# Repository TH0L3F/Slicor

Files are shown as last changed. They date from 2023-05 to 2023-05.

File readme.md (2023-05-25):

#  Slicor

Trancheuse de sable pour conçue pour le laboratoire de Sciences Naturelles de l'université de Lille

## Objectif

Trancher des blocs de sable de manière précise et sécuritaire pour faire un mapping 3D de ceux-ci afin de les étudier.

--------------------

## Construction

La trancheuse est constitué d'une structure rigide permettant d'interconnecter toute les parties mécanique utiles en un unique objet d'étude. Cette structure possède une plateau en métal sur lequel le bloc de sable doit se déplacer. Pour limiter les frottements il a était décidé de mettre une plaque en verre qui est lubrifier avant chaques utilisations. Pour absorber les chocs et limiter l'influence des variations de niveaux du plan en métal sur la plaque de verre (qui pourrait la fragiliser voir même la casser) une plaque en caoutchouc se trouve entre les deux plaques.

Une plaque mobile quand à elle permet de pousser le bloc de sable afin de le faire glisser sur la plaque en verre préalablement cité. Celui-ci est mis en mouvement par un vérin électrique. Un encodeur linéaire permet quand à lui de connaitre la position de la plaque à tous moment. Cette régle permet de mesurer des pats de déplacements dans un sens ou l'autre mais ne donne pas de référentiel c'est pourquoi un premier contacteur mécanique se trouve à l'extrémité zéro de la machine. Un second permet de savoir quand la plaque arrive en fin de course. Le vérin est contrôlé par un driver de moteur à courant continu lui même contrôler par une carte électronique (kicad de la carte dans le dossier électronique) permettant de récupérer les informations de tous les composants cités précédèment.

Un pupitre permet de faire l'interface homme-machine avec 3 voyants, respectivement : STOP (rouge), EN MOUVEMENT (JAUNE) et PRET (VERT) ainsi que deux boutons AVANT et ARRIERE. Un pavet numérique permet de sélectionner des valeurs avec un touche pour valider et 4 touches (A B C et D) permettant d'utiliser des valeurs preselectionnés. Un écran permet enfin d'afficher toute les informations nécessaires. Tous ces composants sont interconnectés via une autre carte électronique (kicad de la carte dans le dossier électronique). Le pupitre contient aussi l'alimentation, un bouton marche arret, et un bouton d'arrêt d'urgence.

Les deux cartes sont interconnectés via une liaison série (RX TX) UART afin permettre dans un sens d'envoyer les ordres et de recevoir dans l'autre sens un feedback de ce qui se passe.

--------------------

## Fonctionnement  

Dans un premier temps l'utilisateur fait le homming de la machine (la mise à zéro) afin que celle-ci se déplace pour se mettre en contact avec le premier contacteur.

Puis l'utilisateur entre une valeur et la valide sur le pavé.

Enfin il peut appuyer sur le bouton AVANT ou ARRIERE afin de déplacer le vérin et donc le bloc de sable de la distance souhaitée.

La valeur de déplacement peut être changer en dehors des moments de mouvements. Il faut alors à nouveau valider.

--------------------

## Préparation

Il faut mettre en position zéro la machine après chaques utilisations pour facilité la préparation de la fois suivante.

Premièrement il faut huiler la plaque de verre pour faciliter le déplacement.

Puis disposer le bloc de sable en buter sur la plaque mobile et le plan perpendiculaire à la plaque mobile.

Puis faire les étapes de fonctionnement précisé ci-dessus.

--------------------

#AUTRE

## Programmation

Pour programmer il faut utiliser un programmateur spécifique et le connecteur correspondant sur la carte. Le programmateur est le même que le programmateur du projet Slicor. Une petite fléche permet sur la carte et le connecteur du programmateur permet de détromper le sens de connexion. Ensuite via l'IDE arduino il est possible de mettre le bootloader ("carte : arduino uno", "programmateur : TINYasISP" puis "burn bootloader") il est nécessaire de mettre le bootloader si la puce n'en a pas déjà. Ensuite avec l'option "programmer via un programmateur" il est possible de téléverser le programmer dans le microcontrôleur.

#### ATTENTION !!!
Avec le programmeteur mis à dispositon une erreur survient dans certaine condition. Si un timeout est émis par le programmateur une solution est d'enlever ou d'ajouter des delay(1) dans la partie setup du programme. (Si une meilleure solution existe je suis preneur).

## TODO

### Mécanique
-Monter les pièces usinés (Douille à bille avec pièce en acier et circlips
-Faire souder la structure porteuse de plateau
-Fixer le plan de pousser sur la structure souder
-Fixer les douilles sur la structure souder
-Fixer les pièces fesant le lien entre la structure souder et le vérin
-Installer les équerres de support des tiges
-Vérifier le positionnement
-Modéliser et fabriquer un support pour l'autre extremité du vérin
-La fixer directement sur la plaque en acier
-Faire le lien entre l'encodeur linéaire et la structure souder (mesure direct de la position)
-Fixer une lame sur le mobile de découpe de façon sécuritaire et précise

#### Attention !!!
-Ne pas retirer les douilles des tiges (ça les abimes)
-Vérifier le parallèlisme avant d'appliquer le moindre effort (sinon la structure risque d'être détruite)
-Traiter le cadre pour limiter les risques de rouilles (milieu humide et sable)

### Programmation
-Vérifier la communication entre les deux cartes
-Programmer le PID (vérin - encodeur linéaire) pour le mouvement de la plaque
-Vérifier le sens des contacteurs

#### Attention !!!
-Faire les premiers tests à vide et toujours à porter de bouton d'arrêt d'urgence
-Programmer avec le même programmateur que le subductor
-Parfois la programmation ne fonctionne pas et nécessite l'ajout ou le retrait de delay(1) à des endroits dans le programme (Dont know why ...)
-Vérifier le sens de branchement des deux contacteurs fin de course

### Manuel
-Modifier le manuel si nécessaire après avoir expérimenté ce qui est actuellement proposé

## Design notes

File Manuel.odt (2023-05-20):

Manuel d'utilisation de la

machine Slicor

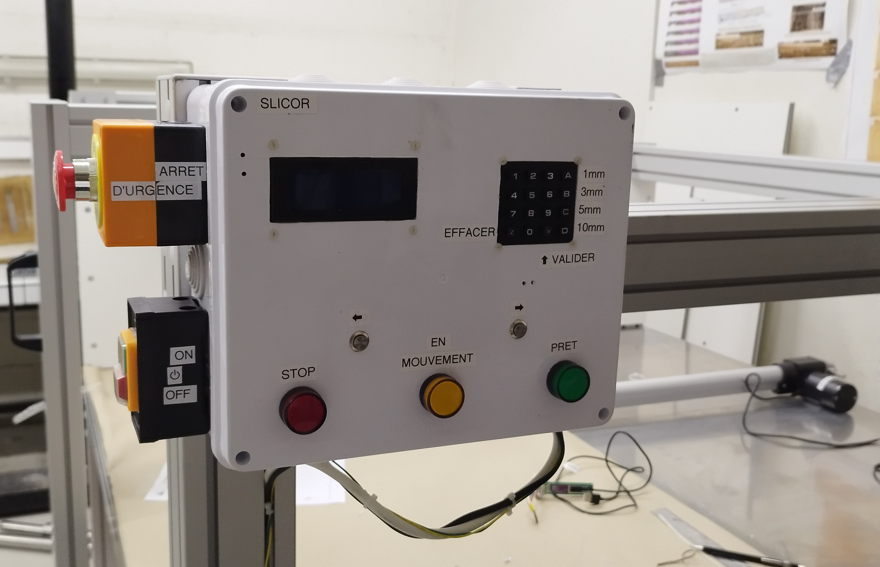
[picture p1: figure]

INTRODUCTION

La machine slicor permet de découper des blocs de sable de différentes tailles en tranche de façon précise. Cette machine est équipée d'un vérin électrique qui pousse le bloc de sable poser sur une plaque de verre qui sera ensuite découpé par l’utilisateur à l’aide d’un mobile sur lequel une lame est attachée.

SÉCURITÉ

La sécurité est primordiale lors de l'utilisation de la machine de découpe de blocs de sable. Voici les mesures à prendre :

1. Ne pas toucher l’intérieur de la machine pendant son fonctionnement.
2. Ne pas dépasser la plage de mouvement.
3. Utiliser le bouton d’arrêt d’urgence en cas de danger ou de problème.
4. Ne pas laisser la machine sans surveillance pendant son utilisation.
5. Ne pas dépasser la charge maximale de la machine (500Kg).

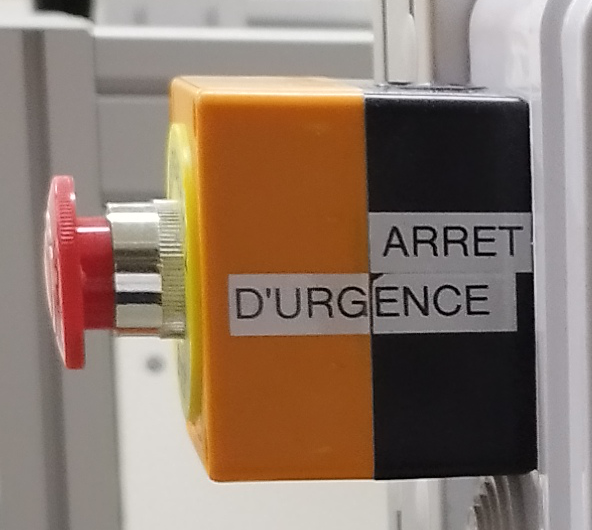
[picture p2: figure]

ÉTAPES DE PREPARATION

Étape 1 : Retirer tout ce qui se trouve autour de la machine et qui pourrait gêner son fonctionnement.

Étape 2 : Vérifier qu'il n'y a rien derrière la plaque (du côté de l'accroche du vérin).

Étape 3 : Nettoyer la surface devant et derrière le plan de poussée de la machine.

Étape 4 : Démarrer la machine.

Étape 5 : Effectuer la procédure de retour à la position initiale de la machine (homing).

Étape 6 : Appliquer une graisse minérale adaptée sur la surface en verre.

Étape 7 : Charger le bloc de sable sur le plan en verre.

Étape 8 : Positionner le bloc de sable contre le plan de poussée.

La machine et le bloc de sable sont maintenant prêts pour le découpage.

ÉTAPES DE TRANCHAGE

Étape 1 : Sélectionner à l'aide du clavier la valeur du déplacement souhaité.

Étape 2 : Vérifier sur l'écran que la valeur souhaitée est bien inscrite.

Étape 3 : Confirmer la valeur en utilisant la touche appropriée du clavier.

Étape 4 : Appuyer sur le bouton avant ou arrière pour déplacer le vérin selon la valeur indiquée

Étape 5 : Effectuer un mouvement aller avec le dispositif de tranchage pour réaliser une tranche.

Étape 6 : Effectuer un mouvement de retour pour replacer le dispositif de tranchage au début de la course.

Pour effectuer plusieurs tranches successives : répéter les étapes 4, 5 et 6 autant de fois que nécessaire tout en veillant à respecter les règles de sécurité.

Pour modifier l'épaisseur des tranches, refaire les étapes 1, 2 et 3.

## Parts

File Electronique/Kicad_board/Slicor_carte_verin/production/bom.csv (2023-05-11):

Designator | Footprint | Quantity | Value | LCSC Part #
C1 | C_Elec_10x10.2 | 1 | 680uF
C2 | C_Elec_10x10.2 | 1 | 220uF
C3, C4 | C_01005_0402Metric | 2 | 22p
D5 | D_SOD-128 | 1 | 1N5824
L1 | L_7.3x7.3_H4.5 | 1 | 33uH
R13 | R_1206_3216Metric | 1 | 100k
U1 | TO-263-5_TabPin3 | 1 | LM2596S-5
Y1 | Crystal_SMD_3225-4Pin_3.2x2.5mm | 1 | 16MHz
uC1 | TQFP-32_7x7mm_P0.8mm | 1 | ATmega328-A

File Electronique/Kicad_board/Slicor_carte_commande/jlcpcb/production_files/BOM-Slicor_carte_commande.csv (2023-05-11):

Comment | Designator | Footprint | LCSC
16MHz | Y1 | Crystal_SMD_3225-4Pin_3.2x2.5mm | C13738
ATmega328-A | uC1 | TQFP-32_7x7mm_P0.8mm | C14877
22p | C3,C4 | C_0402_1005Metric | C1555
100k | R13 | R_1206_3216Metric | C17900
10k | R1,R2 | R_1206_3216Metric | C17902
2k | R3,R4,R5 | R_1206_3216Metric | C17944
LM2596S-5 | U1 | TO-263-5_TabPin3 | C194349
S8050 | Q1,Q2,Q3 | SOT-23-3 | C2146
Shottky 24 5V | D5 | D_SOD-128 | C2766156
680uF | C1 | C_Elec_10x10.2 | C335987
220uF | C2 | C_Elec_10x10.2 | C393833
1k | R6 | R_1206_3216Metric | C4410
33uH | L1 | L_7.3x7.3_H4.5 | C514809
LED | D1 | LED_0805_2012Metric | C84256
TestPoint | TP4 | TestPoint_Pad_1.5x1.5mm
TestPoint | TP3 | TestPoint_Pad_1.5x1.5mm
TestPoint | TP2 | TestPoint_Pad_1.5x1.5mm
TestPoint | TP1 | TestPoint_Pad_1.5x1.5mm
Connecteur_Alim | J1 | TerminalBlock_bornier-2_P5.08mm
Connecteur_bouton_1 | J5 | JST_XH_B2B-XH-A_1x02_P2.50mm_Vertical
Connecteur_led_3 | J9 | JST_XH_B2B-XH-A_1x02_P2.50mm_Vertical
Connecteur_ecran | J2 | JST_XH_B4B-XH-A_1x04_P2.50mm_Vertical
Connecteur_Prog | J4 | PinHeader_1x08_P2.54mm_Vertical
Connecteur_led_2 | J8 | JST_XH_B2B-XH-A_1x02_P2.50mm_Vertical
Connecteur_clavier_1 | J3 | JST_XH_S4B-XH-A_1x04_P2.50mm_Horizontal
MountingHole_Pad | H1 | MountingHole_4.3mm_M4_DIN965_Pad
Connecteur_communication | J10 | JST_XH_B2B-XH-A_1x02_P2.50mm_Vertical
Connecteur_led_1 | J7 | JST_XH_B2B-XH-A_1x02_P2.50mm_Vertical
MountingHole_Pad | H4 | MountingHole_4.3mm_M4_DIN965_Pad
Connecteur_bouton_2 | J6 | JST_XH_B2B-XH-A_1x02_P2.50mm_Vertical
MountingHole_Pad | H3 | MountingHole_4.3mm_M4_DIN965_Pad
MountingHole_Pad | H2 | MountingHole_4.3mm_M4_DIN965_Pad
Connecteur_clavier_2 | J11 | JST_XH_S4B-XH-A_1x04_P2.50mm_Horizontal

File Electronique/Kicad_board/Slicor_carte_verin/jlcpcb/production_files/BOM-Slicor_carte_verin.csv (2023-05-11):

Comment | Designator | Footprint | LCSC
16MHz | Y1 | Crystal_SMD_3225-4Pin_3.2x2.5mm | C13738
ATmega328-A | uC1 | TQFP-32_7x7mm_P0.8mm | C14877
22p | C3,C4 | C_01005_0402Metric | C1555
100k | R13 | R_1206_3216Metric | C17900
10k | R1,R2 | R_1206_3216Metric | C17902
LM2596S-5 | U1 | TO-263-5_TabPin3 | C194349
1N5824 | D5 | D_SOD-128 | C2766156
680uF | C1 | C_Elec_10x10.2 | C335987
220uF | C2 | C_Elec_10x10.2 | C393833
33uH | L1 | L_7.3x7.3_H4.5 | C514809
Conn_encodeur_linear | J5 | JST_XH_B4B-XH-A_1x04_P2.50mm_Vertical
Connecteur_Comm | J3 | JST_XH_B2B-XH-A_1x02_P2.50mm_Vertical
Conn_mot_2 | J7 | JST_XH_B4B-XH-A_1x04_P2.50mm_Vertical
Conn_mot_1 | J6 | JST_XH_B4B-XH-A_1x04_P2.50mm_Vertical
Connecteur_Moteur | J2 | TerminalBlock_bornier-2_P5.08mm
MountingHole_Pad | H2 | MountingHole_4mm_Pad_Via
Connecteur_Alim | J1 | TerminalBlock_bornier-2_P5.08mm
MountingHole_Pad | H4 | MountingHole_4mm_Pad_Via
MountingHole_Pad | H1 | MountingHole_4mm_Pad_Via
Connecteur_Prog | J4 | PinHeader_1x08_P2.54mm_Vertical
MountingHole_Pad | H3 | MountingHole_4mm_Pad_Via
Conn_contacteur_A | J9 | JST_XH_B2B-XH-A_1x02_P2.50mm_Vertical
Conn_contacteur_B | J8 | JST_XH_B2B-XH-A_1x02_P2.50mm_Vertical

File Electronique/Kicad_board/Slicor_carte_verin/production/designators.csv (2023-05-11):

C1:1
C2:1
C3:1
C4:1
D5:1
H1:1
H2:1
H3:1
H4:1
J1:1
J2:1
J3:1
J4:1
J5:1
J6:1
J7:1
L1:1
R13:1
U1:1
Y1:1
uC1:1

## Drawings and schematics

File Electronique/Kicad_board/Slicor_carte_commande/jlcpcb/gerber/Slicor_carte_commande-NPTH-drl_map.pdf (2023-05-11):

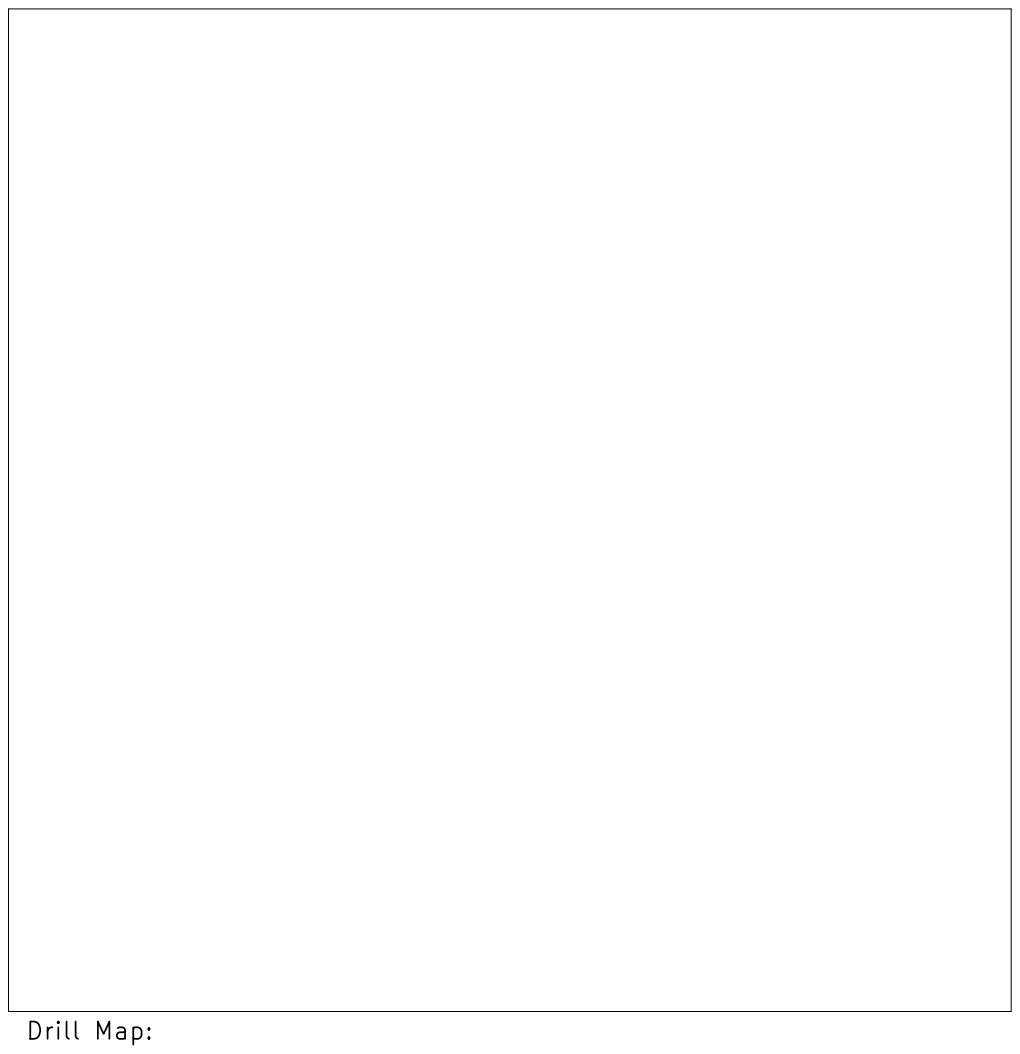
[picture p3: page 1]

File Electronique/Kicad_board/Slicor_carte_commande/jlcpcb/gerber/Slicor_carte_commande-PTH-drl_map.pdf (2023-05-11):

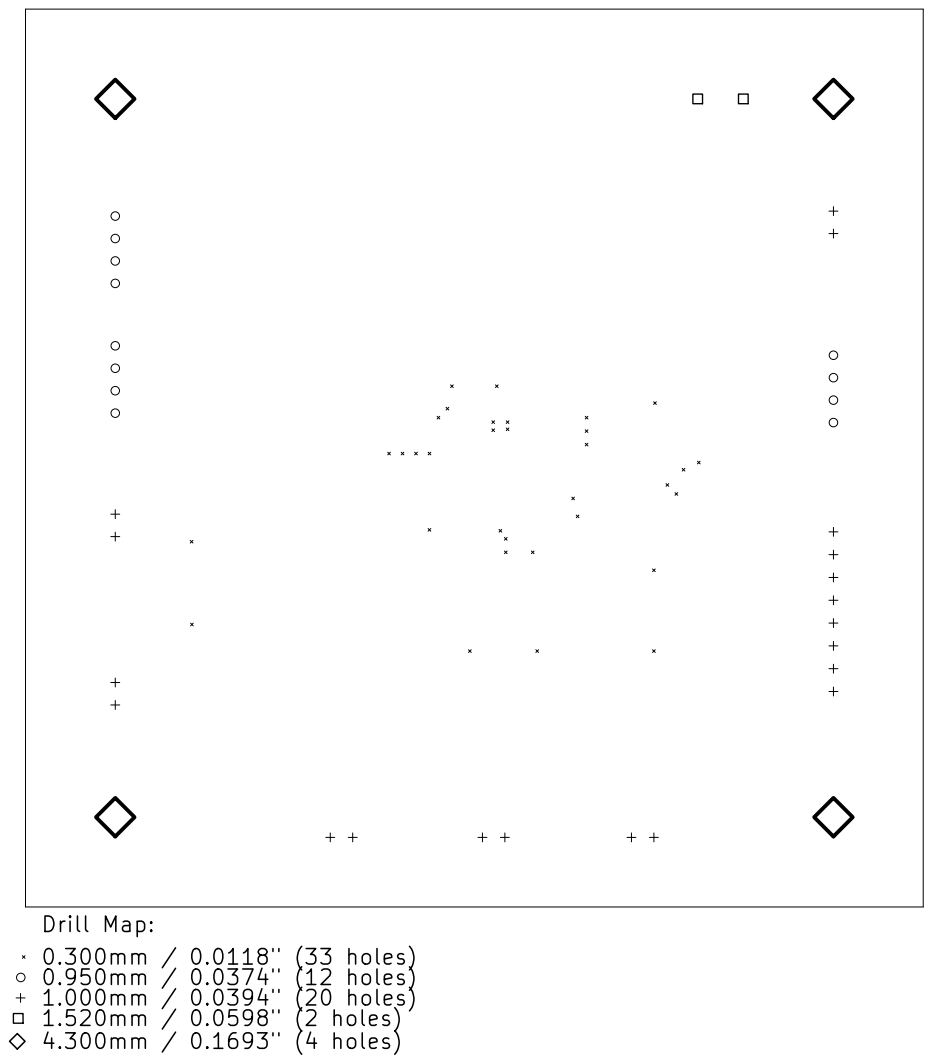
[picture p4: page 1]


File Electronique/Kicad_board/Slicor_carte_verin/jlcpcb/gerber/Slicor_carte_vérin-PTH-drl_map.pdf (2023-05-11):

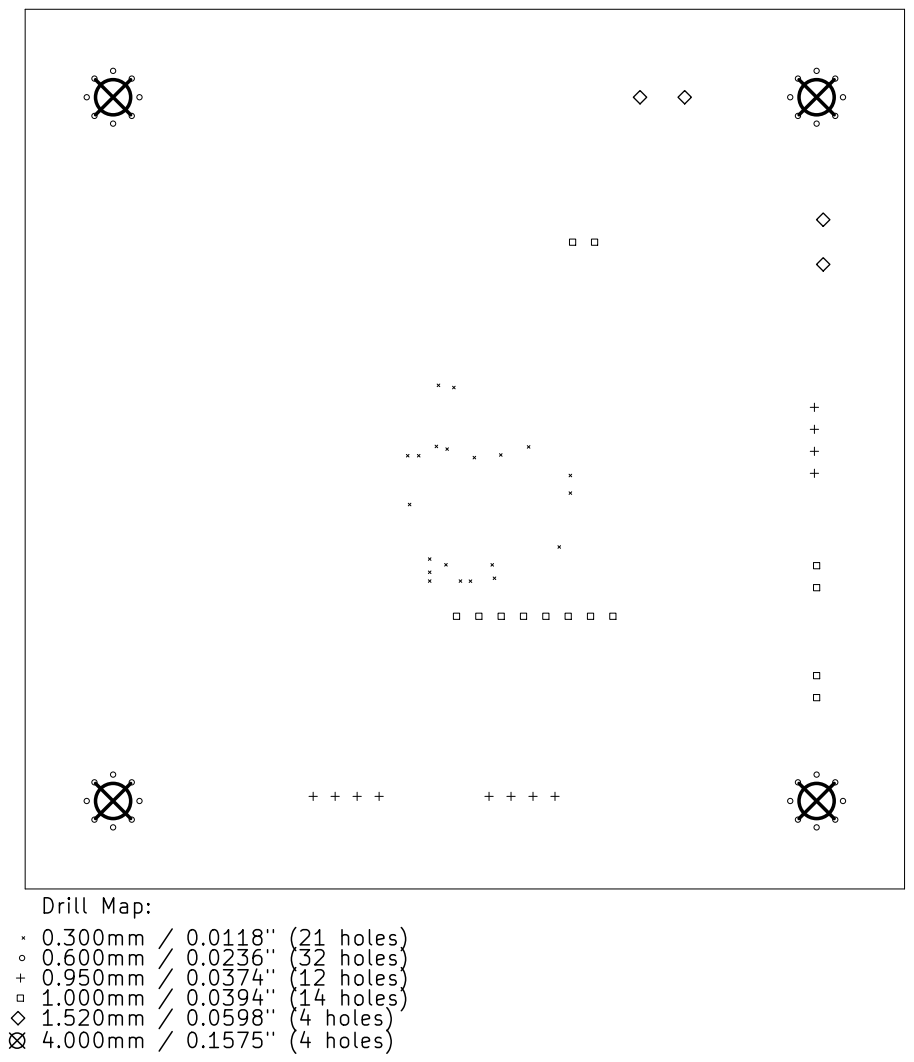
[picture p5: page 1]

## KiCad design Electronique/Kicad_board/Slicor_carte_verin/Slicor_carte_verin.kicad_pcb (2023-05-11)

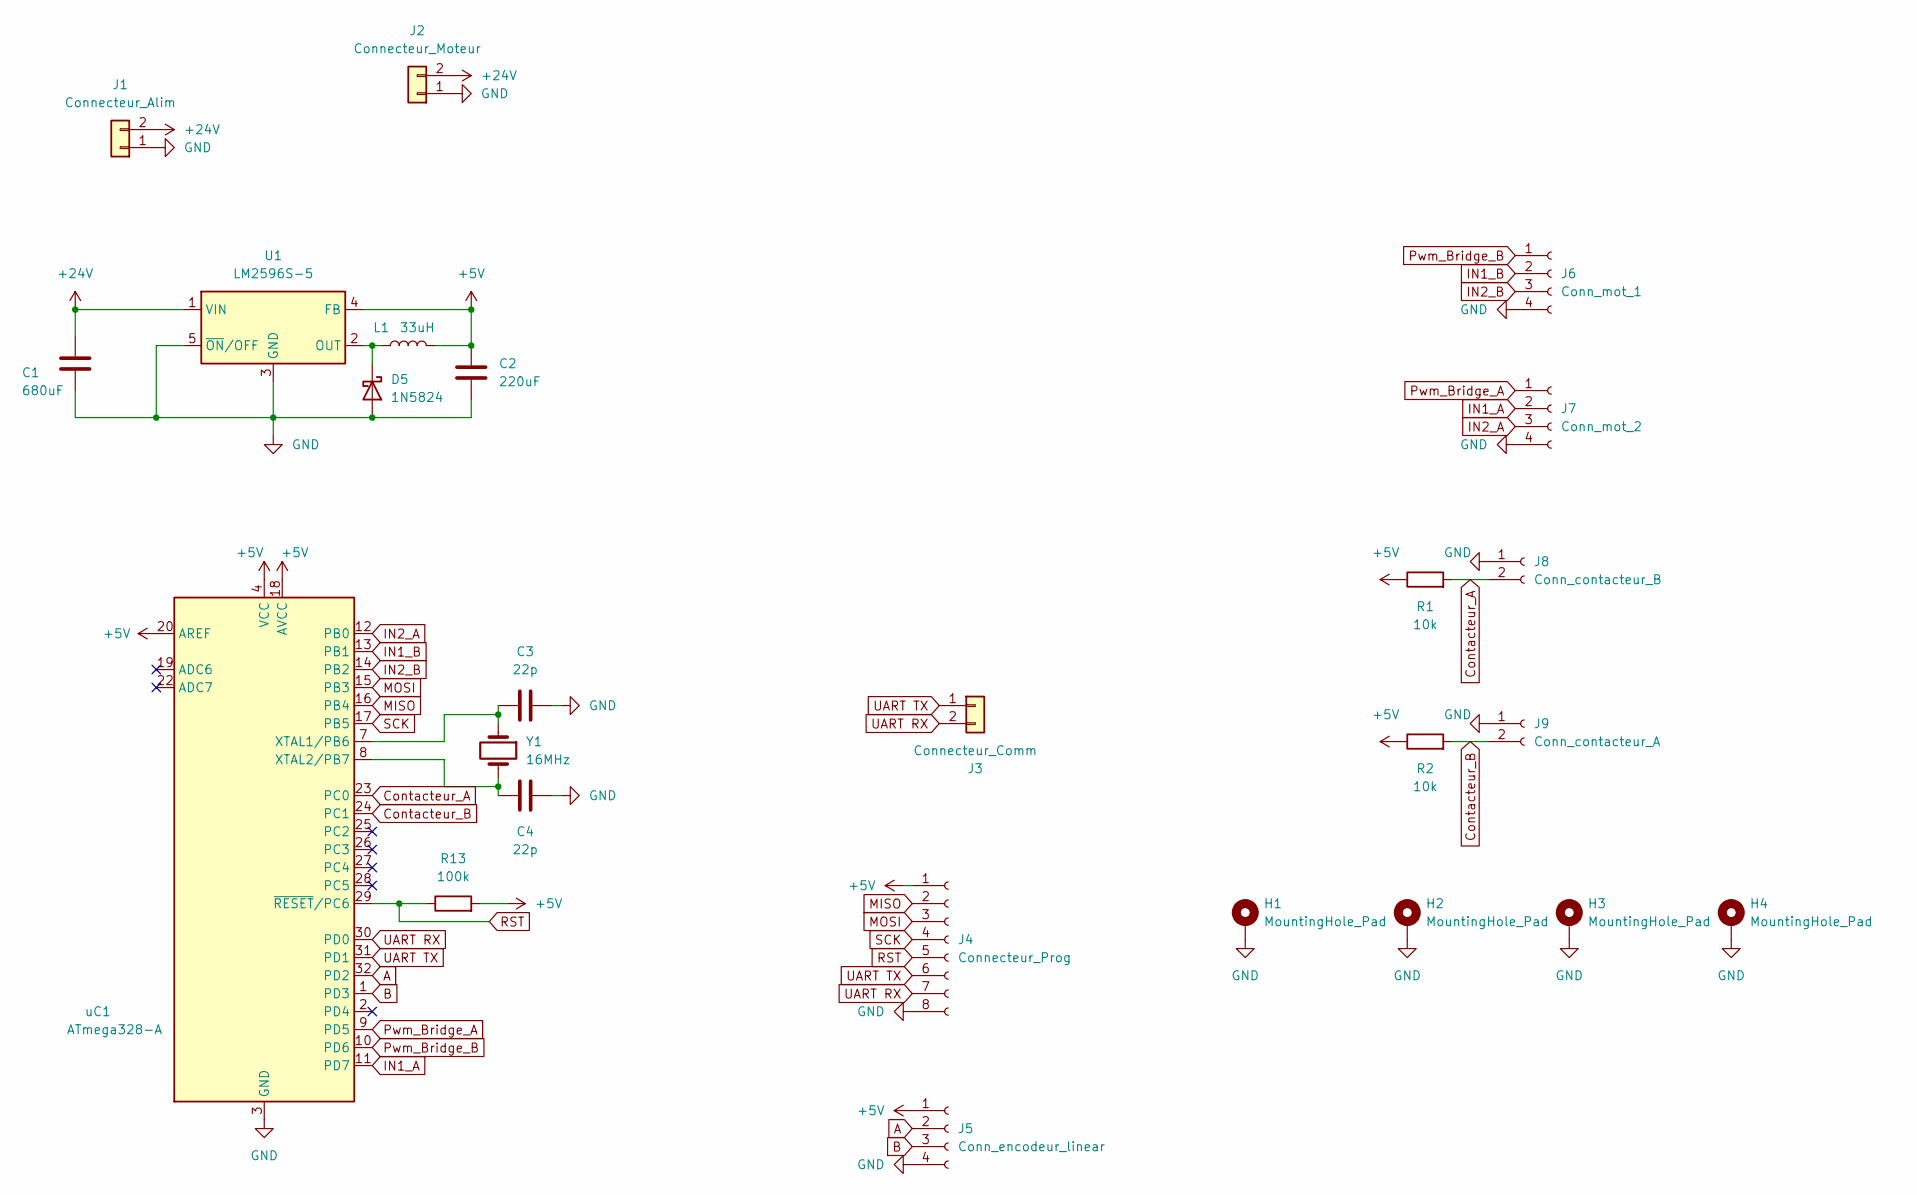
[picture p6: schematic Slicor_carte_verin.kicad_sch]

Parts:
C1: 680uF; C_Elec_10x10.2
C2: 220uF; C_Elec_10x10.2
C3, C4: 22p; C_01005_0402Metric
D5: 1N5824; D_SOD-128
H1, H2, H3, H4: MountingHole_Pad; MountingHole_4mm_Pad_Via
J1: Connecteur_Alim; TerminalBlock_bornier-2_P5.08mm
J2: Connecteur_Moteur; TerminalBlock_bornier-2_P5.08mm
J3: Connecteur_Comm; JST_XH_B2B-XH-A_1x02_P2.50mm_Vertical
J4: Connecteur_Prog; PinHeader_1x08_P2.54mm_Vertical
J5: Conn_encodeur_linear; JST_XH_B4B-XH-A_1x04_P2.50mm_Vertical
J6: Conn_mot_1; JST_XH_B4B-XH-A_1x04_P2.50mm_Vertical
J7: Conn_mot_2; JST_XH_B4B-XH-A_1x04_P2.50mm_Vertical
J8: Conn_contacteur_B; JST_XH_B2B-XH-A_1x02_P2.50mm_Vertical
J9: Conn_contacteur_A; JST_XH_B2B-XH-A_1x02_P2.50mm_Vertical
L1: 33uH; L_7.3x7.3_H4.5
R1, R2: 10k; R_1206_3216Metric
R13: 100k; R_1206_3216Metric
U1: LM2596S-5; TO-263-5_TabPin3
Y1: 16MHz; Crystal_SMD_3225-4Pin_3.2x2.5mm
uC1: ATmega328-A; TQFP-32_7x7mm_P0.8mm

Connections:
+5V: C2.1, J4.1, J5.1, L1.2, R1.1, R2.1, R13.2, U1.4 (FB), uC1.4 (VCC), uC1.6 (VCC), uC1.18 (AVCC), uC1.20 (AREF)
+24V: C1.1, J1.2, J2.2, U1.1 (VIN)
A: J5.2, uC1.32 (PD2)
B: J5.3, uC1.1 (PD3)
Contacteur_A: J8.2, R1.2, uC1.23 (PC0)
Contacteur_B: J9.2, R2.2, uC1.24 (PC1)
GND: C1.2, C2.2, C3.2, C4.2, D5.2 (A), H1.1, H2.1, H3.1, H4.1, J1.1, J2.1, J4.8, J5.4, J6.4, J7.4, J8.1, J9.1, U1.3 (GND), U1.5 (~ON/OFF), uC1.3 (GND), uC1.5 (GND), uC1.21 (GND)
IN1_A: J7.2, uC1.11 (PD7)
IN1_B: J6.2, uC1.13 (PB1)
IN2_A: J7.3, uC1.12 (PB0)
IN2_B: J6.3, uC1.14 (PB2)
MISO: J4.2, uC1.16 (PB4)
MOSI: J4.3, uC1.15 (PB3)
unnamed: C3.1, Y1.1, uC1.7 (XTAL1/PB6)
unnamed: C4.1, Y1.2, uC1.8 (XTAL2/PB7)
unnamed: D5.1 (K), L1.1, U1.2 (OUT)
Pwm_Bridge_A: J7.1, uC1.9 (PD5)
Pwm_Bridge_B: J6.1, uC1.10 (PD6)
RST: J4.5, R13.1, uC1.29 (~RESET/PC6)
SCK: J4.4, uC1.17 (PB5)
UART RX: J3.2, J4.7, uC1.30 (PD0)
UART TX: J3.1, J4.6, uC1.31 (PD1)

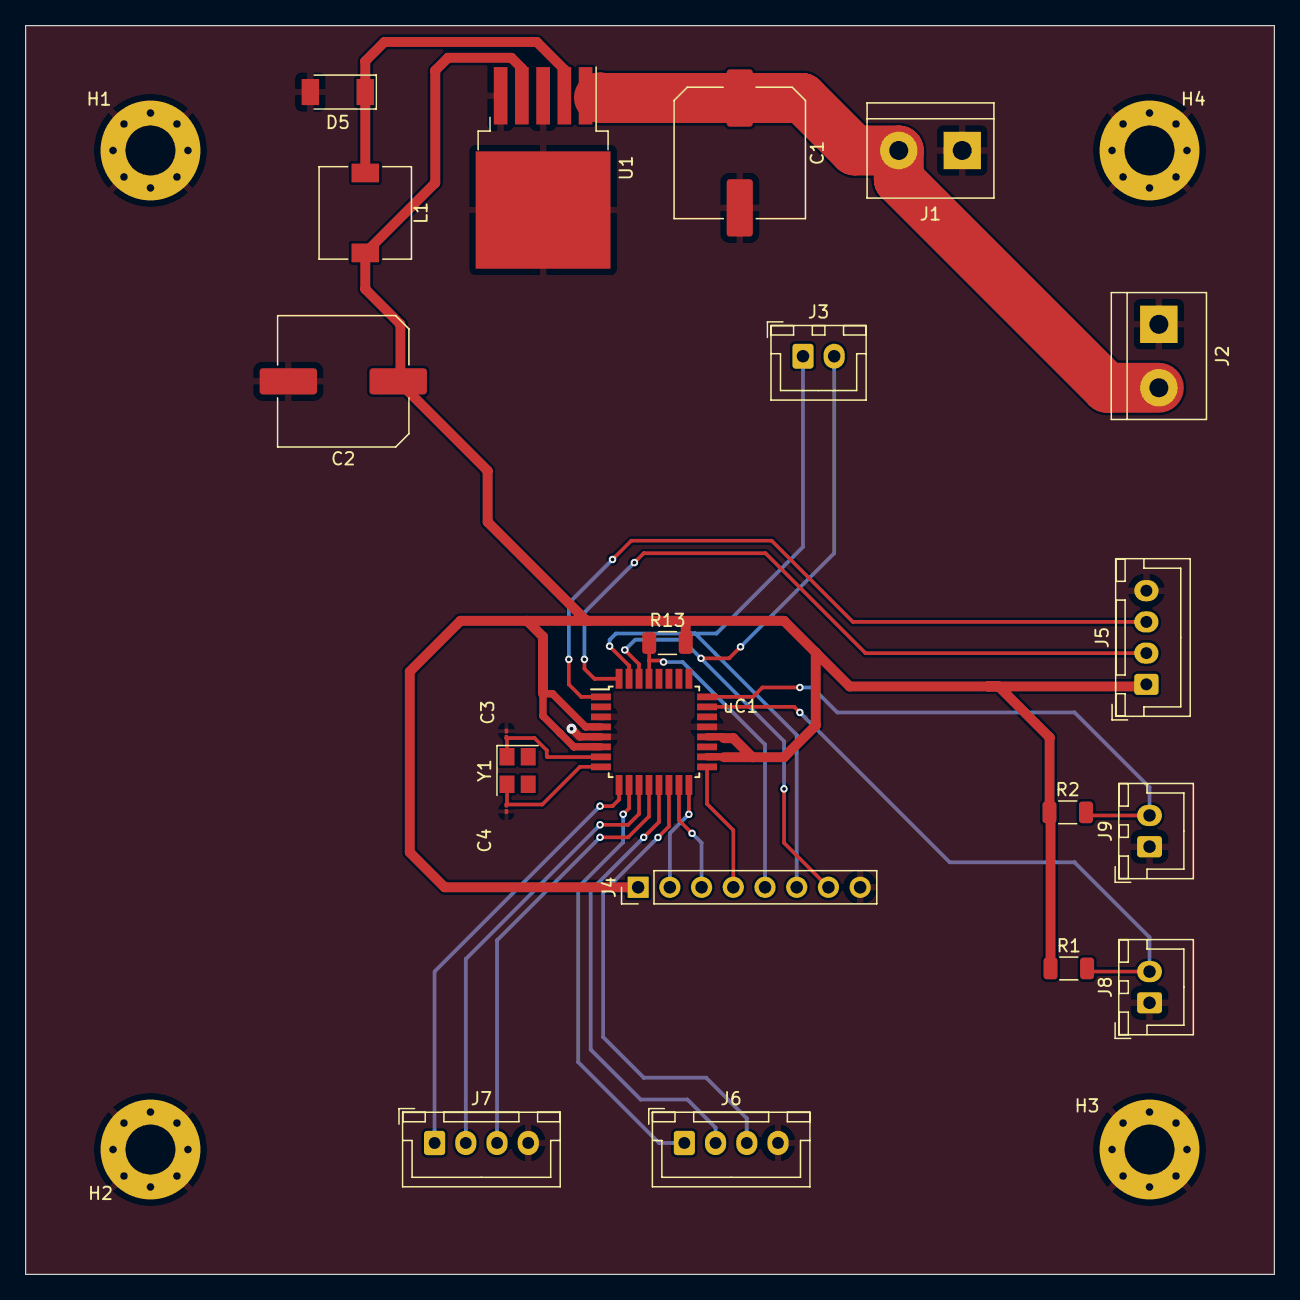
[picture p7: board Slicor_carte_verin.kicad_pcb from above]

Board: 4 copper layers, 100.0 x 100.0 mm, 25 parts (0 on the bottom side), 22 nets.

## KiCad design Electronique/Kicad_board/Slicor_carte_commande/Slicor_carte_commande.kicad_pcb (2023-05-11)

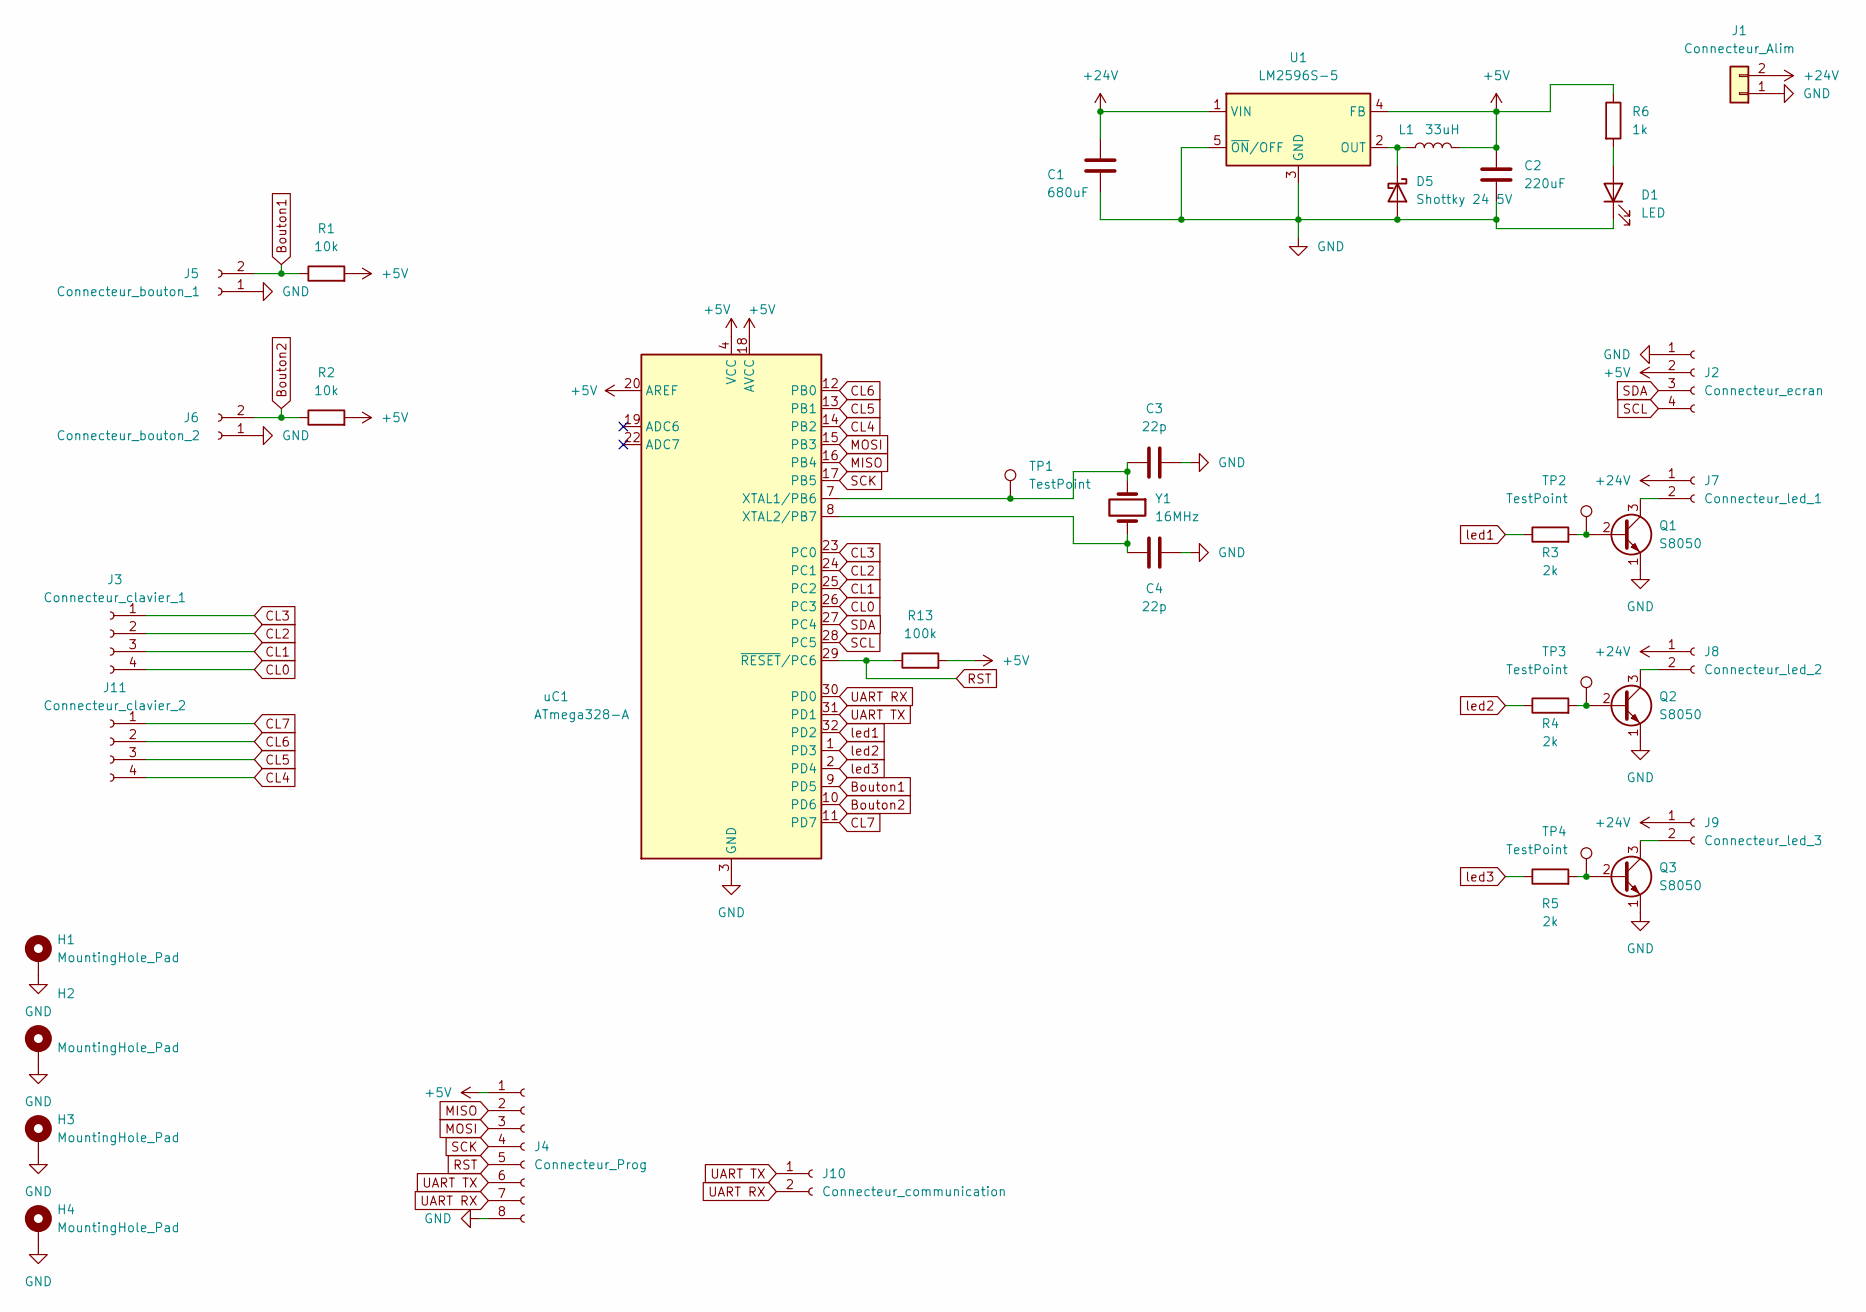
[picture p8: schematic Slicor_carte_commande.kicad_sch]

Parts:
C1: 680uF; C_Elec_10x10.2
C2: 220uF; C_Elec_10x10.2
C3, C4: 22p; C_0402_1005Metric
D1: LED; LED_0805_2012Metric
D5: Shottky 24 5V; D_SOD-128
H1, H2, H3, H4: MountingHole_Pad; MountingHole_4.3mm_M4_DIN965_Pad
J1: Connecteur_Alim; TerminalBlock_bornier-2_P5.08mm
J2: Connecteur_ecran; JST_XH_B4B-XH-A_1x04_P2.50mm_Vertical
J3: Connecteur_clavier_1; JST_XH_S4B-XH-A_1x04_P2.50mm_Horizontal
J4: Connecteur_Prog; PinHeader_1x08_P2.54mm_Vertical
J5: Connecteur_bouton_1; JST_XH_B2B-XH-A_1x02_P2.50mm_Vertical
J6: Connecteur_bouton_2; JST_XH_B2B-XH-A_1x02_P2.50mm_Vertical
J7: Connecteur_led_1; JST_XH_B2B-XH-A_1x02_P2.50mm_Vertical
J8: Connecteur_led_2; JST_XH_B2B-XH-A_1x02_P2.50mm_Vertical
J9: Connecteur_led_3; JST_XH_B2B-XH-A_1x02_P2.50mm_Vertical
J10: Connecteur_communication; JST_XH_B2B-XH-A_1x02_P2.50mm_Vertical
J11: Connecteur_clavier_2; JST_XH_S4B-XH-A_1x04_P2.50mm_Horizontal
L1: 33uH; L_7.3x7.3_H4.5
Q1, Q2, Q3: S8050; SOT-23-3
R1, R2: 10k; R_1206_3216Metric
R3, R4, R5: 2k; R_1206_3216Metric
R6: 1k; R_1206_3216Metric
R13: 100k; R_1206_3216Metric
TP1, TP2, TP3, TP4: TestPoint; TestPoint_Pad_1.5x1.5mm
U1: LM2596S-5; TO-263-5_TabPin3
Y1: 16MHz; Crystal_SMD_3225-4Pin_3.2x2.5mm
uC1: ATmega328-A; TQFP-32_7x7mm_P0.8mm

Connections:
+5V: C2.1, J2.2, J4.1, L1.2, R1.2, R2.2, R6.1, R13.2, U1.4 (FB), uC1.4 (VCC), uC1.6 (VCC), uC1.18 (AVCC), uC1.20 (AREF)
+24V: C1.1, J1.2, J7.1, J8.1, J9.1, U1.1 (VIN)
Bouton1: J5.2, R1.1, uC1.9 (PD5)
Bouton2: J6.2, R2.1, uC1.10 (PD6)
CL0: J3.4, uC1.26 (PC3)
CL1: J3.3, uC1.25 (PC2)
CL2: J3.2, uC1.24 (PC1)
CL3: J3.1, uC1.23 (PC0)
CL4: J11.4, uC1.14 (PB2)
CL5: J11.3, uC1.13 (PB1)
CL6: J11.2, uC1.12 (PB0)
CL7: J11.1, uC1.11 (PD7)
GND: C1.2, C2.2, C3.2, C4.2, D1.1 (K), D5.2 (A), H1.1, H2.1, H3.1, H4.1, J1.1, J2.1, J4.8, J5.1, J6.1, Q1.1 (E), Q2.1 (E), Q3.1 (E), U1.3 (GND), U1.5 (~ON/OFF), uC1.3 (GND), uC1.5 (GND), uC1.21 (GND); also elsewhere on the board
MISO: J4.2, uC1.16 (PB4)
MOSI: J4.3, uC1.15 (PB3)
unnamed: C3.1, TP1.1, Y1.1, uC1.7 (XTAL1/PB6)
unnamed: C4.1, Y1.2, uC1.8 (XTAL2/PB7)
unnamed: D1.2 (A), R6.2
unnamed: D5.1 (K), L1.1, U1.2 (OUT)
unnamed: J7.2, Q1.3 (C)
unnamed: J8.2, Q2.3 (C)
unnamed: J9.2, Q3.3 (C)
unnamed: Q1.2 (B), R3.2, TP2.1
unnamed: Q2.2 (B), R4.2, TP3.1
unnamed: Q3.2 (B), R5.2, TP4.1
RST: J4.5, R13.1, uC1.29 (~RESET/PC6)
SCK: J4.4, uC1.17 (PB5)
SCL: J2.4, uC1.28 (PC5)
SDA: J2.3, uC1.27 (PC4)
UART RX: J4.7, J10.2, uC1.30 (PD0)
UART TX: J4.6, J10.1, uC1.31 (PD1)
led1: R3.1, uC1.32 (PD2)
led2: R4.1, uC1.1 (PD3)
led3: R5.1, uC1.2 (PD4)

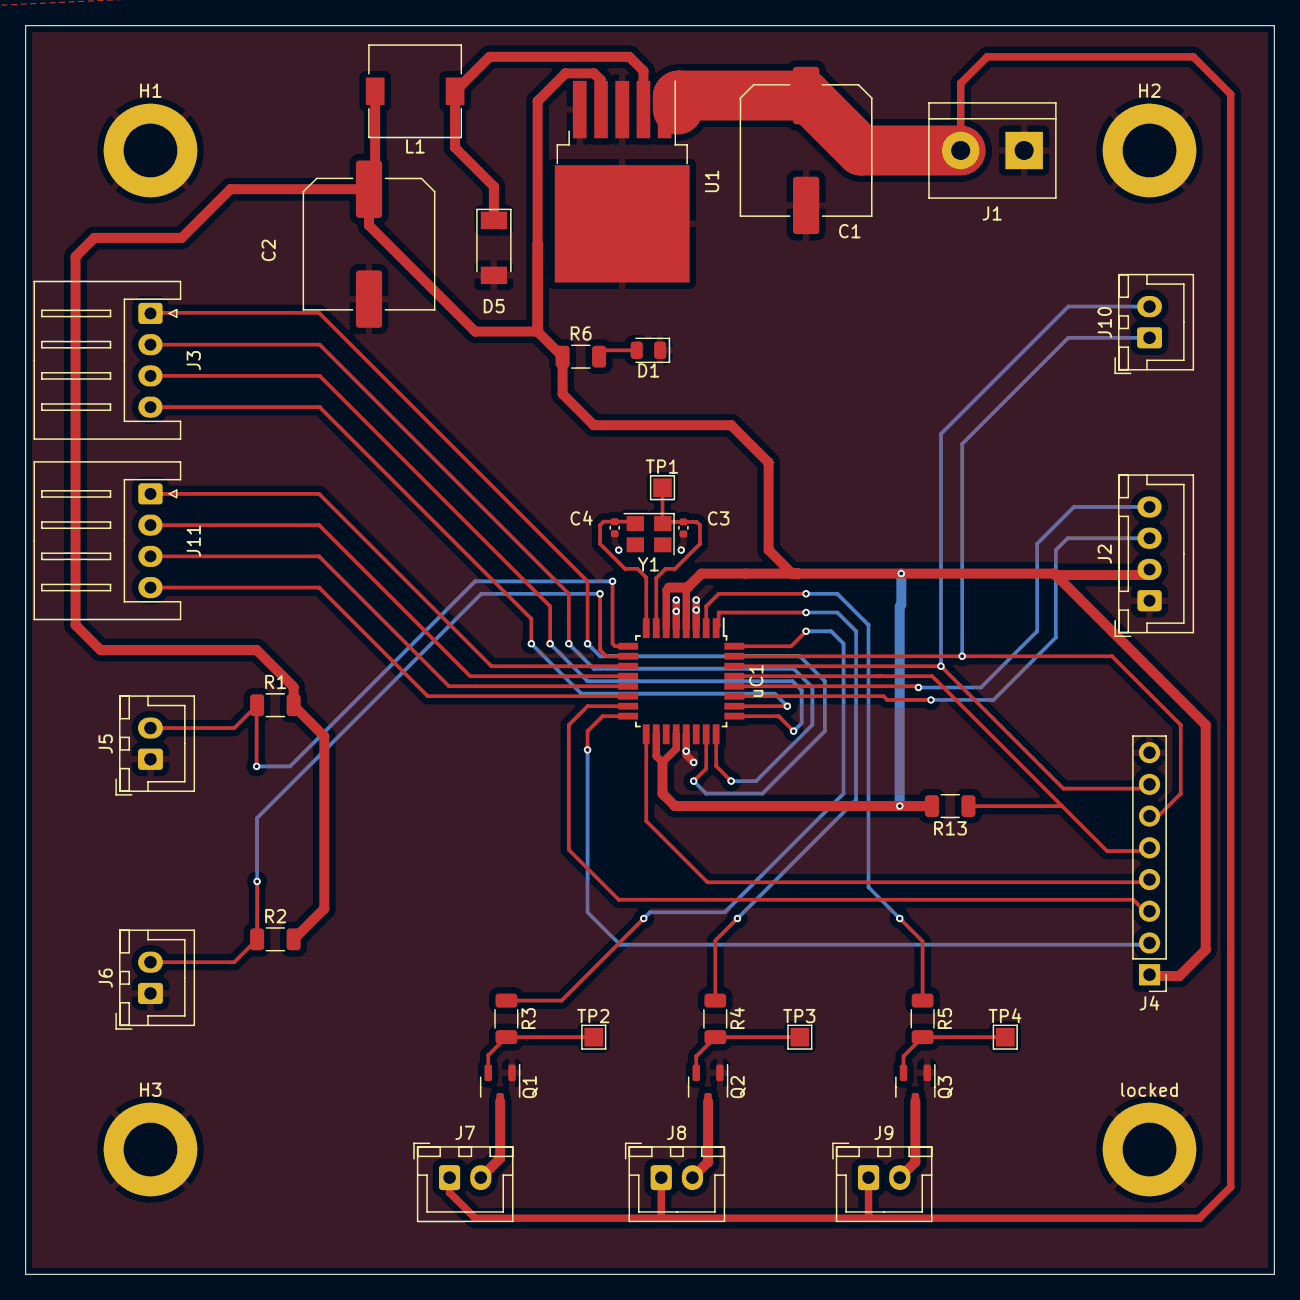
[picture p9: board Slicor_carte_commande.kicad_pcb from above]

Board: 4 copper layers, 100.0 x 100.0 mm, 39 parts (0 on the bottom side), 34 nets.

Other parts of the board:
locked: MountingHole_Pad; MountingHole_4.3mm_M4_DIN965_Pad

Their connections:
GND: locked.1; also elsewhere on the board

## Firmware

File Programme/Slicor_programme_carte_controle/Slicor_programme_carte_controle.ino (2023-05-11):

//Utilitaire pour l'écran LCD
#include <Wire.h> 
#include <LiquidCrystal_I2C.h>
#define len_lcd 20 //Nombre de caractère en longueur de l'écran
#define high_lcd 4 //Nombre de lignes de l'écran
#define lcd_adress 0x27 //Adresse de l'écran
LiquidCrystal_I2C lcd(lcd_adress,len_lcd,high_lcd);  //Configurer l'écran 
int screen_type = 0; //Permet de connaitre le mode d'affichage actuel
bool screen_chg = 0; //Permet de savoir si il y a eu changement sur l'écran

//Utilitaire du clavier
//#include <MultitapKeypad.h>
#define COL0 7 //Définition des broches du clavier
#define COL1 8 
#define COL2 9
#define COL3 10 
#define ROW3 A3 
#define ROW2 A2 
#define ROW1 A1 
#define ROW0 A0 
char clv [4][4] = {
  {'1','2','3','A'},
  {'4','5','6','B'},
  {'7','8','9','C'},
  {'*','0','#','D'}
};
char key = 0;
char key_last = 0;

//MultitapKeypad kpd( ROW0, ROW1, ROW2, ROW3, COL0, COL1, COL2, COL3 ); //Création de l'objet du clavier
//Key key; //Création de l'objet touche étant un sous ensemble du clavier
int max_value = 100; //La valeur maximale qui peut être tapper à la main
bool preset = 0; //Permet de faire la distinction entre une valeur prédéfinie et une valeur tapper au clavier.

//Utilitaire voyant
int state = 0; //-1 en cours de homing
               // 0 pour le voyant rouge signifiant que la machine ne connait pas sa position, qu'elle est en fin de course ou qu'il y a une erreur.
               // 1 pour le voyant orange signifiant que la machine est en mouvement.
               // 2 pour le voyant vert signifiant que la machine est à l'arrêt et connait sa position (et qu'il n'y a pas d'erreur).        
#define V1 4 //pin voyant vert
#define V2 3 //pin voyant orange
#define V3 2 //pin voyant rouge
bool vchg = 0; //Permet de savoir si il y a eu un changement au niveau des voyants

//Utilitaire bouton
#define B1 5 //pin bouton avancé
#define B2 6 //pin bouton reculé
const int buttonPin1 = 2; // Broche du bouton 1
const int buttonPin2 = 3; // Broche du bouton 2
int buttonState1 = 0; // État du bouton 1
int buttonState2 = 0; // État du bouton 2
unsigned long lastButtonPress = 0; // Moment du dernier appui sur un bouton
int delay_btn = 300;
unsigned long antispam = 0; // Moment du dernier appui sur un bouton
int delay_antispam = 1500;

//Variables communiquées entre les deux cartes
int pos = -1; //Contient la position du vérin à un instant donné en mm
int mouvement = 0; //Longueur du prochain mouvement en mm
char inByte = 0;

//Variables de delay
unsigned long timer1 = 0; //Permet de limiter la fréquence d'affichage écran et voyants
int delay_timer1 = 1000;

void setup(){
  //Démarrer le port série
  Serial.begin(9600);

  //Démarrer l'écran LCD
  lcd.init();  //initialize the lcd
  lcd.backlight();  //open the backlight 
   
  //Affichage au démarrage
  screen(screen_type);

  //Configuration du clavier
  pinMode(COL0,INPUT_PULLUP);
  pinMode(COL1,INPUT_PULLUP);
  pinMode(COL2,INPUT_PULLUP);
  pinMode(COL3,INPUT_PULLUP);
  pinMode(ROW0,OUTPUT);
  pinMode(ROW1,OUTPUT);
  pinMode(ROW2,OUTPUT);
  pinMode(ROW3,OUTPUT);

  //Configuration des voyants
  pinMode(V1,OUTPUT); //Mettre pins des voyants en sortie
  pinMode(V2,OUTPUT);
  pinMode(V3,OUTPUT);
  
  //Configuration des boutons
  pinMode(B1,INPUT);
  pinMode(B2,INPUT);

  //Päuse pour l'affichage et laisser le temps aux composants de démarrer
  delay(3000);

  screen_type = 1;
  vchg = 1;
  screen_chg = 1;

  delay(1);
  delay(1);
  delay(1);
  delay(1);
  delay(1);
  delay(1);
  
}

void loop(){
  if(screen_chg){
    screen(screen_type); //Mise à jour de l'écran
    screen_chg = 0;
  }
  if(vchg){
    voyants(); //Mise à jour des voyants
    vchg = 0;
  }
  mes_puiss_read();
  if(pos != -1){
    clavier(); //Mise à jour du clavier
  }
  bouton(); //Mise à jour des boutons
}

char keyget(){
  int row = 0;

  digitalWrite(ROW0,LOW);
  digitalWrite(ROW1,HIGH);
  digitalWrite(ROW2,HIGH);
  digitalWrite(ROW3,HIGH);
  row = 0;
  if(!digitalRead(COL0)) return clv[row][0];
  if(!digitalRead(COL1)) return clv[row][1];
  if(!digitalRead(COL2)) return clv[row][2];
  if(!digitalRead(COL3)) return clv[row][3];

  digitalWrite(ROW0,HIGH);
  digitalWrite(ROW1,LOW);
  digitalWrite(ROW2,HIGH);
  digitalWrite(ROW3,HIGH);
  row = 1;
  if(!digitalRead(COL0)) return clv[row][0];
  if(!digitalRead(COL1)) return clv[row][1];
  if(!digitalRead(COL2)) return clv[row][2];
  if(!digitalRead(COL3)) return clv[row][3];

  digitalWrite(ROW0,HIGH);
  digitalWrite(ROW1,HIGH);
  digitalWrite(ROW2,LOW);
  digitalWrite(ROW3,HIGH);
  row = 2;
  if(!digitalRead(COL0)) return clv[row][0];
  if(!digitalRead(COL1)) return clv[row][1];
  if(!digitalRead(COL2)) return clv[row][2];
  if(!digitalRead(COL3)) return clv[row][3];

  digitalWrite(ROW0,HIGH);
  digitalWrite(ROW1,HIGH);
  digitalWrite(ROW2,HIGH);
  digitalWrite(ROW3,LOW);
  row = 3;
  if(!digitalRead(COL0)) return clv[row][0];
  if(!digitalRead(COL1)) return clv[row][1];
  if(!digitalRead(COL2)) return clv[row][2];
  if(!digitalRead(COL3)) return clv[row][3];

  return 0;

}

void clavier(){ //Gère le clavier
  key = keyget();
  if((key != key_last) && (key != 0)){  
    if(key == 'A'){ //Mettre le voyant en orange  //Preselection A
      mouvement = 1;
      state = 4; 
    }
    else if(key == 'B'){//Preselection B
      mouvement = 3;
      state = 4;
    }  
    else if(key == 'C'){//Preselection C
      mouvement = 5;
      state = 4;
    }  
    else if(key == 'D'){//Preselection D
      mouvement = 10;
      state = 4;
    }  
    else if(key == '*'){//Effacer
      mouvement = 0;
      state = 4;
    }
    else if(key == '#'){//Valider
      state = 2;
    }
    else if((key <= '9') && (key >= '0')){ //Entrer une valeur précise
      state = 4;
      mouvement = mouvement*10+(key-'0');
      if(mouvement > 500){
        mouvement = 500;
      }
    }
    screen_chg = 1;
    vchg = 1;
  }
  key_last = key;
}

void bouton(){ //Gère les boutons
  unsigned long currentMillis = millis(); // Obtenir le temps écoulé depuis le démarrage de la carte Arduino
  buttonState1 = digitalRead(B1); // Lire l'état du bouton 1
  buttonState2 = digitalRead(B2); // Lire l'état du bouton 2

  if((currentMillis - antispam) > delay_antispam){ //Comme le nom l'indique cela évite que la commande soit spammé
    if (buttonState1 == LOW && buttonState2 == HIGH) { // Si le bouton 1 est appuyé et le bouton 2 est relâché
      if (currentMillis - lastButtonPress > delay_btn) { // Si le dernier appui sur un bouton remonte à plus de 50 millisecondes
        //Serial.println("Bouton 1 appuyé"); // Afficher un message de débogage
        antispam = millis();
        mes_puiss_send(1);
        lastButtonPress = currentMillis; // Mettre à jour le moment du dernier appui sur un bouton
      }
    } 
    else if (buttonState1 == HIGH && buttonState2 == LOW) { // Si le bouton 1 est relâché et le bouton 2 est appuyé
      if (currentMillis - lastButtonPress > delay_btn) { // Si le dernier appui sur un bouton remonte à plus de 50 millisecondes
        //Serial.println("Bouton 2 appuyé"); // Afficher un message de débogage
        antispam = millis();
        mes_puiss_send(2);
        lastButtonPress = currentMillis; // Mettre à jour le moment du dernier appui sur un bouton
      }
    }
    else if (buttonState1 == LOW && buttonState2 == LOW) { // Si les deux boutons sont appuyés
      if (currentMillis - lastButtonPress > delay_btn) { // Si le dernier appui sur un bouton remonte à plus de 50 millisecondes
        //Serial.println("Les deux boutons sont appuyés"); // Afficher un message de débogage
        antispam = millis();
        vchg = 1; //Précise qu'il y a peut etre eu un changement au niveau des voyants
        screen_type = 2; //Change ou confirme le mode de l'écran
        screen_chg = 1;//Précisé qu'il y a peut etre eu un changement au niveau de l'écran
        mes_puiss_send(3);
        lastButtonPress = currentMillis; // Mettre à jour le moment du dernier appui sur un bouton
        state = -1; //Position inconnu
      }
    }
    else{
      lastButtonPress = millis();
    }
  }
  return 0;
}

void voyants(){ //Gère les voyants
  if(state == 0){ //Allumage du voyant 1
    digitalWrite(V1,HIGH);
    digitalWrite(V2,LOW);
    digitalWrite(V3,LOW);
  }
  else if(state == 1 || state == -1 || state == 4){ //Allumage du voyant 2
    digitalWrite(V1,LOW);
    digitalWrite(V2,HIGH);
    digitalWrite(V3,LOW);    
  }
  else if(state == 2 || state == 3){ //Allumage du voyant 3
    digitalWrite(V1,LOW);
    digitalWrite(V2,LOW);
    digitalWrite(V3,HIGH);    
  }
  return;
}

void mes_puiss_send(int mes){ //Gère les messages avec la carte de puissance
  switch(mes){
    case 0: 
      break; //Envoi rien du tout
    case 1:
      if(state == 2){
        Serial.print("m1"+String(mouvement));//Envoi le message de mouvement dans le sens 1
      }
      break;
    case 2:
      if(state == 2){
        Serial.print("m2"+String(mouvement));//Envoi le message de mouvement dans le sens 1
      }
      break;        
    case 3:
      if(state == 0 || state == 2){
        Serial.print("h");//Envoi le message de homing
        break;
      }
  }
  return;
}

void mes_puiss_read(){
  if(Serial.available() > 0) {
    inByte = Serial.read();//On lit le premier caractère pour connaitre le type du message
    if(inByte == 'p'){//Alors il s'agit d'un envoi de position
      if(Serial.available() && (char)Serial.peek() != '\n'){
        pos = 0;
        screen_chg = 1;
        vchg = 1;
      }
      while(Serial.available() && (char)Serial.peek() != '\n'){
        pos = pos * 10 + (Serial.read() - '0');
      } 
    }
    else if(inByte == 'r'){//Alors la carte de puissance indique qu'elle est prête à recevoir une nouvelle commande
      screen_chg = 1;
      vchg = 1;
      state = 2;
    }
    else if(inByte == 'm'){//Alors la carte de puissance indique qu'elle est en mouvement
      screen_chg = 1;
      vchg = 1;
      state = 1;      
    }
    else if(inByte == 's'){//Alors la carte de puissance indique qu'elle a atteind le fin de course
      screen_chg = 1;
      vchg = 1;
      state = 0;
    }
    else if(inByte == 'e'){//Alors la carte de puissance indique qu'il y a eu une erreur
      screen_chg = 1;
      vchg = 1;
      state = 3;
    }
  }
}

void screen(int mode){
  if(mode == 0){ //Ecran de démarrage
    lcd.setCursor(0,0);//On remet le curseur en haut à gauche
    lcd.clear();//On efface l'écran avant d'afficher de nouvelles informations
    affichage(0,"Slicor en cours",1);
    affichage(1,"de demarrage.",1);
    affichage(2,"Patientez...",1);
    affichage(3,"Fait par TH0L3F",1);
  }
  else if(mode == 1){ //Ecran avant le homing
    lcd.setCursor(0,0);//On remet le curseur en haut à gauche
    lcd.clear();//On efface l'écran avant d'afficher de nouvelles informations
    affichage(0,"En attente de",1);
    affichage(1,"Homing. Appuyez",1);
    affichage(2,"simultanement sur",1);
    affichage(3,"le bouton <- et ->",1);
  }
  else if(mode == 2){ //Ecran d'affichage en cours de fonctionnement
    lcd.clear();//On efface l'écran avant d'afficher de nouvelles informations
    affichage(0, "Position : ",2);
    if(pos == -1){//Position non connue
      affichage(0,"xxx",3); //Affichage d'un point d'interrogation
    }
    else{//Position connue
      affichage(0,String(pos),3);//Affichage de la position
    }
    affichage(1, "Longueur : ",2);
    affichage(1, String(mouvement)+" mm",3);
    if (state == -1){
      affichage(3, "  En cours de homing",2);
    }
    else if(state == 0){
      affichage(3, "   En bout de course",2);
    }
    else if(state == 1){
      affichage(3, "        En mouvement",2);
    }
    else if(state == 2){
      affichage(3, "         En position",2);
    }
    else if(state == 3){
      affichage(3, "  Erreur, pb machine",2);
    }
    else if(state == 4){
      affichage(3, "   Validez la valeur",2);
    }
  }
}
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

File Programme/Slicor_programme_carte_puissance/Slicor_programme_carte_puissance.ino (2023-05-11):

//*****COMMUNICATION*******
//Variables communiquées entre les deux cartes
int n_error = 0;
int pos_vol = 0; //Position voulue
int delay_send_pos = 1000;
unsigned long last_time = 0;

//*********VERIN***********
//Broches vérin
#define pin_pwm 5 //Pin de contrôle de la vitesse
#define pin_sens 7 //Pin de contrôle dans le sens A
bool sens_abs = true;//Permet d'échanger tous les sens si besoin

//**********REL************
//Broches régle électronique linéaire (rel)
#define rel_A 2 //Pin A du rel
#define rel_B 3 //Pin B du rel

//Variables rel
float dpp = 0.005; // dpp (distance per pulsion) in micrometer
int pos_rel = 157; //Enregistrement de la position de la règle (en pulsion)
bool ax = false; //Ancien état de la broche A
bool bx = false; //Ancien état de la broche B
bool a = false; //Nouvel état de la broche A
bool b = false; //Nouvel état de la broche B

//*****FIN DE COURSE*******
#define fca A0 //Pin fin de course A (position minimal)
#define fcb A1 //Pin fin de course B (position maximale)
bool unk = false; //Si unk vaut false : la position n'est pas connu. Il faut faire un homing

void setup(){

  //Démarrer le port série
  Serial.begin(9600);

  //Configuration du vérin
  pinMode(pin_sens,OUTPUT); //Pin de sens vérin
  pinMode(pin_pwm,OUTPUT); //Pin de sens vérin
  
  //Configuration capteur position linéaire
  attachInterrupt(digitalPinToInterrupt(rel_A), cpl_pos, CHANGE); //Permet de créer des interruption pour la lecture du rel
  attachInterrupt(digitalPinToInterrupt(rel_B), cpl_pos, CHANGE); //Uniquement sur les passages à l'état haut

  pinMode(fca, INPUT_PULLUP);
  pinMode(fcb, INPUT_PULLUP);

  //Activation des interruptions
  interrupts();

  delay(1);
  delay(1);
  delay(1);
  delay(1);
  delay(1);
  delay(1);
  delay(1);
  delay(1);

}

void loop(){
  if (Serial.available()) { // Vérifie si des données sont disponibles sur le port série
    char message = Serial.read(); // Lit le premier caractère reçu sur le port série
    if (message == 'h') {
      Serial.print('h');
      homing(); // Exécute la fonction homming()
      Serial.print('r');
    }
    else if (message == 'm') {
      char direction = Serial.read(); // Lit le caractère suivant
      int length = 0;

      // Lit les caractères suivants jusqu'à ce qu'on atteigne la fin de ligne
      while (Serial.available() && (char)Serial.peek() != '\n') {
        length = length * 10 + (Serial.read() - '0');
      }

      Serial.read(); // Lit le caractère de fin de ligne
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

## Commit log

2023-05-20 Ajout de la liste des choses qui restent à faire
2023-05-21 ajout au readme la méthode de programmation
